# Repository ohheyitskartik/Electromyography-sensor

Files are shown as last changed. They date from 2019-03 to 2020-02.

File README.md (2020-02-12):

# Electromyography-sensor
The following sensor design can amplify, filter &amp; rectify EMG potentials range between less than 50 μV and up to 30 mV  to a 0-3V logic level compatible with arduino's and arm processors inbuilt adc logic level. Open Readme file for more info.

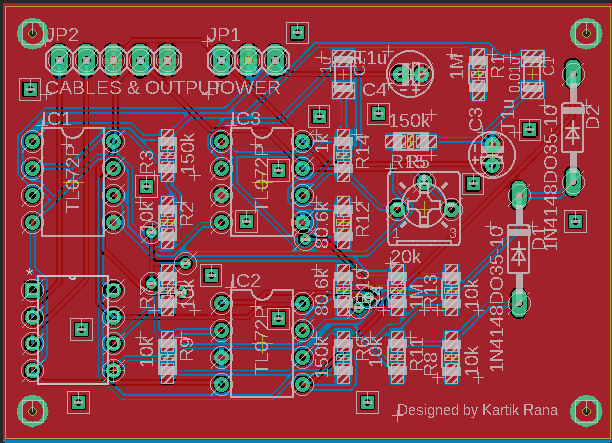
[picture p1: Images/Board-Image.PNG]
Circuit Board


The above mentioned circuit contains :-
1) Differential Op-amp (G=110).
2) Active high pass-filter set at 106.6 Hz.
3) Active low pass-filter set at 1.97 KHz.
4) Active rectification to avoid any damage to your microcontroller from negative voltages.
5) A variable gain at end to control output voltage.

The git contains :- 
- Schematic of the circuit (.Eagle file).
- PCB Design (.Eagle file).
- Parts list with packages and names (.TXT file).
- Images for the breadboard version of the device, PCB design, cad render and output screenshots.

The putput of the device was taken using NI mydaq device - 
Without any muscle movement (placement on forearm).
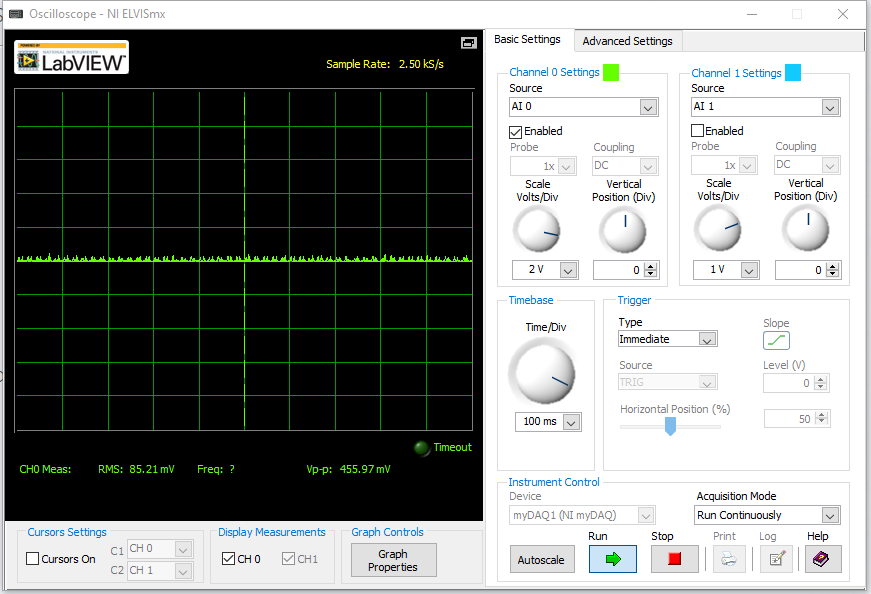
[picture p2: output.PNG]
output without tiggering the muscle


With muscle movement (placement on forearm).
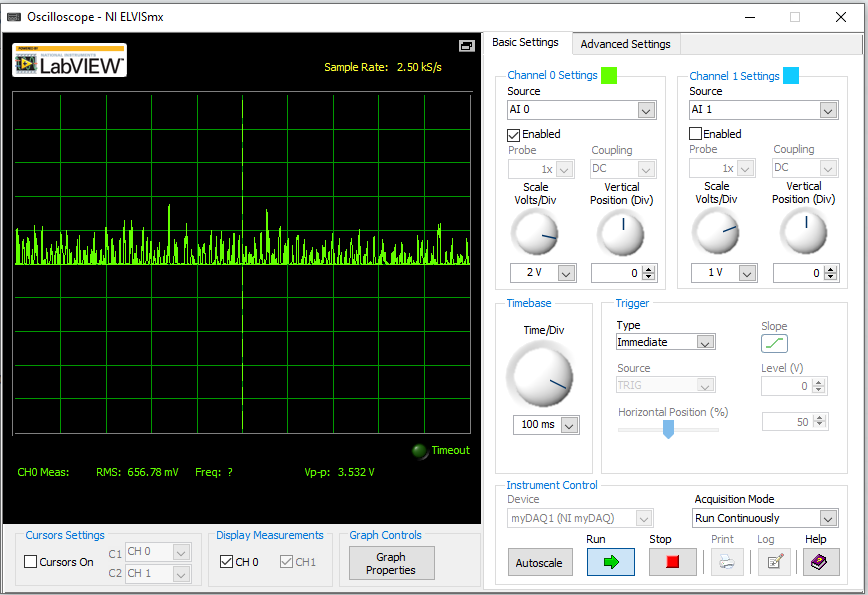
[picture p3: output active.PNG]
output with triggering muscle


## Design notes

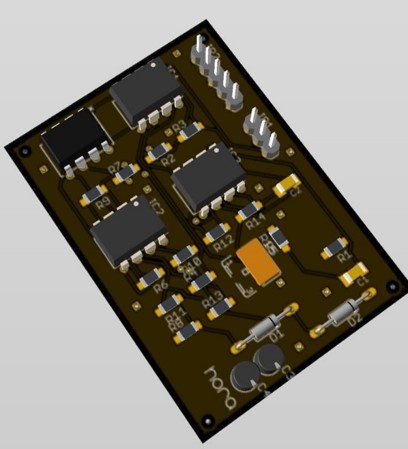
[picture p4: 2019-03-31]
Images/3D render image.jpg

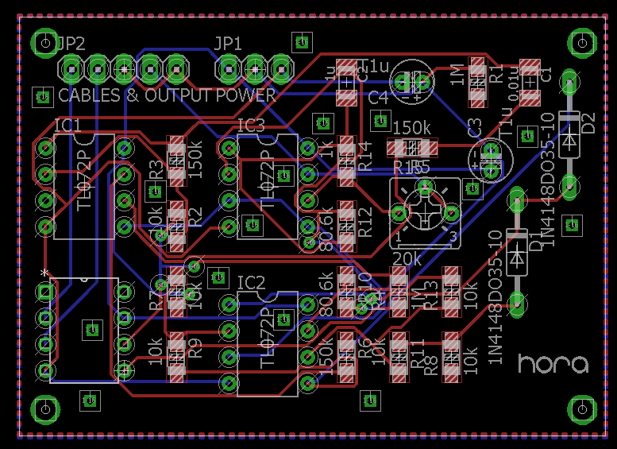
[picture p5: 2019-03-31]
Images/Board Image.png

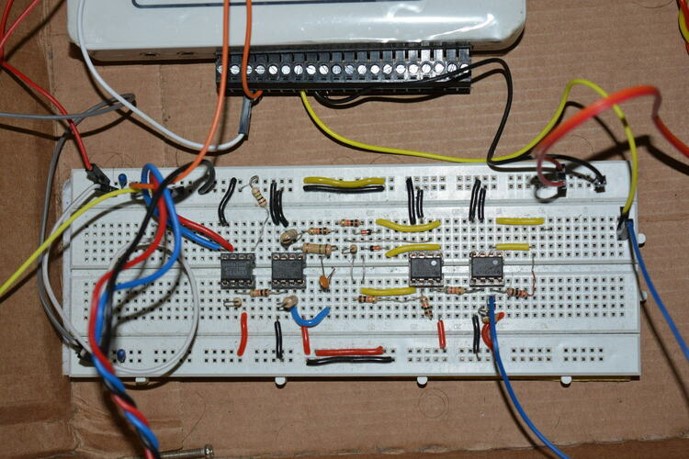
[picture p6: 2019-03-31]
Images/Breadboard Image.jpg

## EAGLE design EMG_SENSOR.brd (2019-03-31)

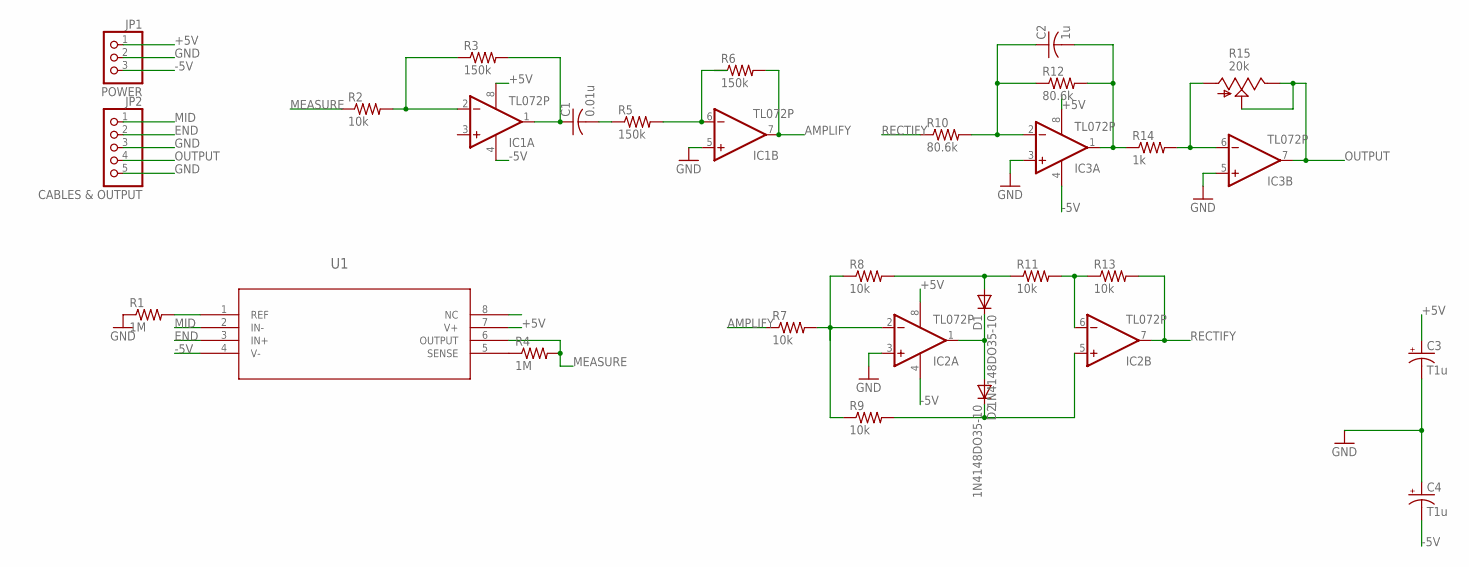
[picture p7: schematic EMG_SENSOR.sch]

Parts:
C1: 0.01u; C1206K
C2: 1u; C1206K; MPN MC0805Y104M500A2.54MM
C3, C4: T1u; E2-4
D1, D2: 1N4148DO35-10; DO35-10
IC1, IC2, IC3: TL072P; DIL08
JP1: POWER; 1X03
JP2: CABLES & OUTPUT; 1X05
R1, R4: 1M; R1206W
R2, R7, R8, R9, R11, R13: 10k; R1206W
R3, R5, R6: 150k; R1206W
R10, R12: 80.6k; R1206W
R14: 1k; R1206W
R15: 20k; B25P
U1: INA106_P_8; P8

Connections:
+5V: C3.+, IC1.8 (V+), IC2.8 (V+), IC3.8 (V+), JP1.1, U1.7 (V+)
-5V: C4.-, IC1.4 (V-), IC2.4 (V-), IC3.4 (V-), JP1.3, U1.4 (V-)
AMPLIFY: IC1.7 (OUT), R6.2, R7.1
END: JP2.2, U1.3 (IN+)
GND: C3.-, C4.+, IC1.5 (+IN), IC2.3 (+IN), IC3.3 (+IN), IC3.5 (+IN), JP1.2, JP2.3, JP2.5, R1.1
MEASURE: R2.1, R4.2, U1.6 (OUTPUT)
MID: JP2.1, U1.2 (IN-)
unnamed: IC2.2 (-IN), R7.2, R9.1
unnamed: IC2.6 (-IN), R11.2, R13.1
unnamed: IC1.2 (-IN), R2.2, R3.1
unnamed: C1.1, IC1.1 (OUT), R3.2
unnamed: C1.2, R5.1
unnamed: R4.1, U1.5 (SENSE)
unnamed: IC1.6 (-IN), R5.2
unnamed: D1.C, D2.A, IC2.1 (OUT)
unnamed: D1.A, R8.2, R11.1
unnamed: C2.1, IC3.2 (-IN), R10.2, R12.1
unnamed: D2.C, IC2.5 (+IN), R9.2
unnamed: C2.2, IC3.1 (OUT), R12.2, R14.1
unnamed: IC3.6 (-IN), R14.2, R15.A
OUTPUT: IC3.7 (OUT), JP2.4, R15.E, R15.S
RECTIFY: IC2.7 (OUT), R10.1, R13.2

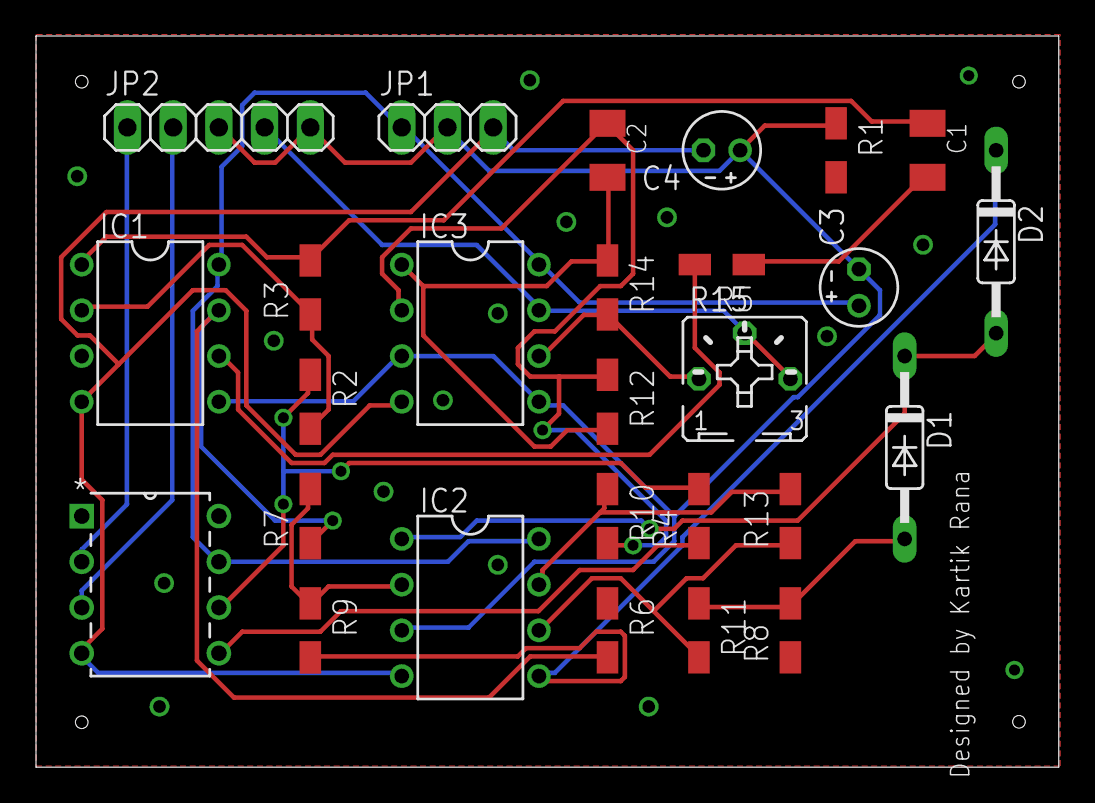
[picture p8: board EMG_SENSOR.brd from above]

Board: 2 copper layers, 56.8 x 40.6 mm, 27 parts (0 on the bottom side), 22 nets.

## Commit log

2019-03-31 Final-task
    Final EMG Board design
    [EMG_SENSOR.brd, EMG_SENSOR.sch]
2019-03-31 Revert "Update EMG_SENSOR.brd"
    This reverts commit 2c1e3195e62d11b7e3e16a25b7b5c478b3a32b3b.
    [EMG_SENSOR.brd]
2019-03-31 Revert "Final-task"
    This reverts commit 8a2adc822e130e4cf756d79e198dd36a2c16bd06.
    [EMG_SENSOR.brd, EMG_SENSOR.sch]
2019-03-31 Final commit
    [EMG_SENSOR.brd, EMG_SENSOR.sch]
